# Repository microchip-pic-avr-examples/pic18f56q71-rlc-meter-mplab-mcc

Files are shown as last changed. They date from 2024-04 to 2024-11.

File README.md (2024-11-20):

<!-- Please do not change this html logo with link -->

<a href="https://www.microchip.com" rel="nofollow">MCHP</a>

# RLC Meter Using the PIC18F56Q71 Microcontroller with MCC Melody

This repository contains an MPLAB® X project, a Resistance, Inductance, Capacitance (RLC) meter implementation using the internal resources of PIC18F56Q71 microcontroller.  
In this code example, the PIC18F56Q71 microcontroller will be used to implement a RLC meter using the Analog-to-Digital Converter (ADC) with Computation and Context, Direct Memory Access (DMA), Timers (TMR0, TMR2, TMR4) and Configurable Logic Cell (CLC) peripherals. The sinusoidal waveform is generated using the Pulse-Width Modulator with Compare (PWM) and other peripherals on the device (DMA, timers). The measurement will be displayed using serial protocols.

**Note**: This project is not an measurement instrument, it was developed only for educational purpose.

## Related Documentation
- [PIC18F56Q71 Product Page](https://www.microchip.com/en-us/product/PIC18F56Q71?utm_source=GitHub&utm_medium=TextLink&utm_campaign=MCU8_PIC18-Q71&utm_content=pic18f56q71-rlc-meter-mplab-mcc-github&utm_bu=MCU08)
- [PIC18F56Q71 Code Examples on Discover](https://mplab-discover.microchip.com/v2?dsl=PIC18F56Q71)
- [PIC18F56Q71 Code Examples on GitHub](https://github.com/microchip-pic-avr-examples/?q=PIC18F56Q71)

## Software Used

- [MPLAB X IDE v6.20 or newer](https://www.microchip.com/en-us/tools-resources/develop/mplab-x-ide?utm_source=GitHub&utm_medium=TextLink&utm_campaign=MCU8_PIC18-Q71&utm_content=pic18f56q71-rlc-meter-mplab-mcc-github&utm_bu=MCU08)
- [MPLAB® XC8 v2.50 or newer](https://www.microchip.com/en-us/tools-resources/develop/mplab-xc-compilers?utm_source=GitHub&utm_medium=TextLink&utm_campaign=MCU8_PIC18-Q71&utm_content=pic18f56q71-rlc-meter-mplab-mcc-github&utm_bu=MCU08)
- [PIC18F-Q_DFP 1.25.433](https://packs.download.microchip.com/)

## Hardware Used

- The [PIC18F56Q71 Curiosity Nano Development board](https://www.microchip.com/en-us/development-tool/EV01G21A?utm_source=GitHub&utm_medium=TextLink&utm_campaign=MCU8_PIC18-Q71&utm_content=pic18f56q71-rlc-meter-mplab-mcc-github&utm_bu=MCU08) is used as a test platform:
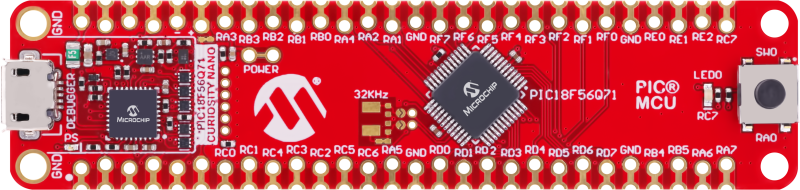
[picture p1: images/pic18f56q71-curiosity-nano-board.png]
    <br>

- [Curiosity Nano Adaptor](https://www.microchip.com/en-us/development-tool/AC164162?utm_source=GitHub&utm_medium=TextLink&utm_campaign=MCU8_PIC18-Q71&utm_content=pic18f56q71-rlc-meter-mplab-mcc-github&utm_bu=MCU08)
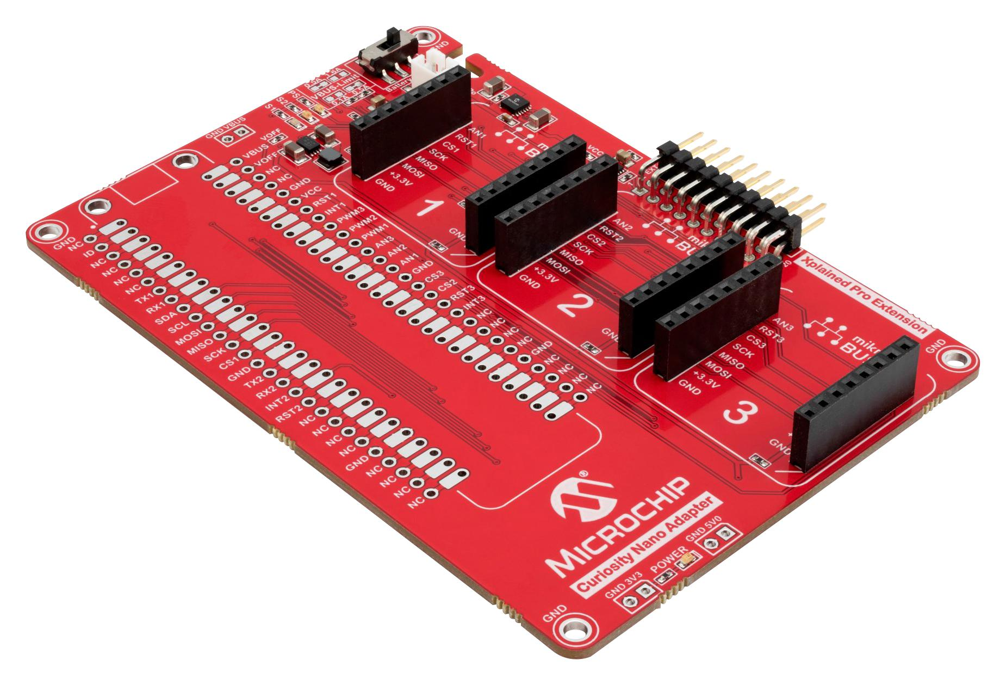
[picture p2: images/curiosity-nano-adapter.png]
    <br>

- [OLED C CLICK Board](https://www.mikroe.com/oled-c-click#/263-clickid-yes) (mikroBUS socket 3)
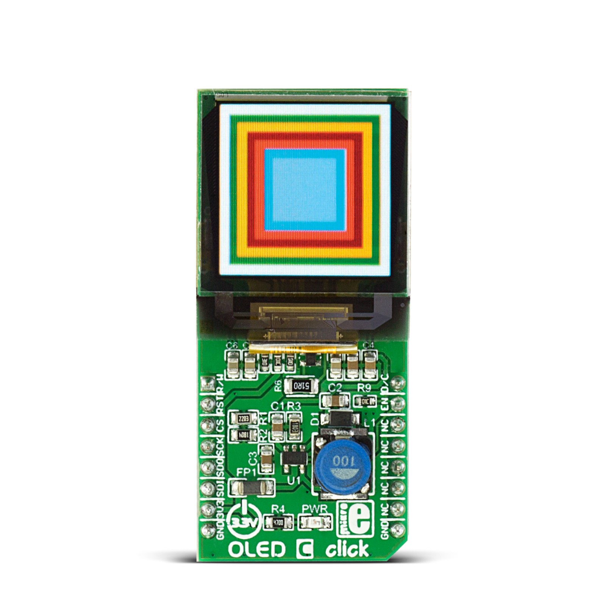
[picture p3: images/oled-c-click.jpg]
    <br>

- RLC Meter Click Board (mikroBUS socket 1)
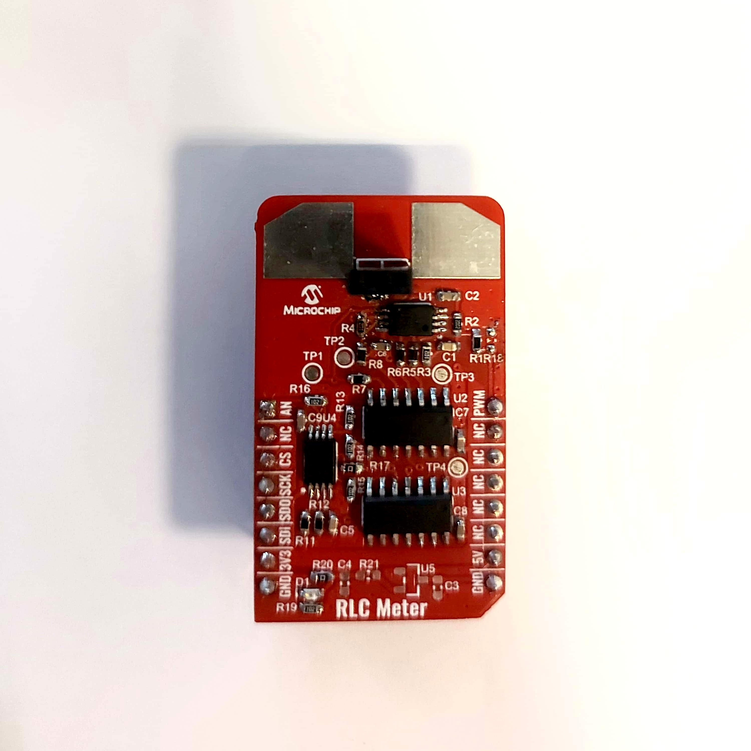
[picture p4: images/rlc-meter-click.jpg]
    <br>

## Operation

To program the Curiosity Nano board with this MPLAB X project, follow the steps provided in the [How to Program the Curiosity Nano Board](#how-to-program-the-curiosity-nano-board) section.

## Concept

RLC meters are measuring instruments that measure a physical property known as impedance. Impedance, which is expressed using the quantifier Z, indicates resistance to the flow of an alternating current (AC). It can be calculated from the current (I) flowing to the measurement target and the voltage (V) across the target’s terminals. Since impedance is expressed as a vector on a complex plane, RLC meters measure not only the ratio of current and voltage RMS values, but also the phase difference between current and voltage waveforms. The result of the measurement is displayed using an OLED display or the UART2 peripheral.

### Measurement Principle

There are different methods used to measure the impedance, each of them with advantages and disadvantages:
- Auto-Balancing Bridge Method
- Resonant Method
- I-V Method

This demo uses an auto-balancing bridge which is the measurement circuit in many RLC meters. The circuit has four terminals, all of which are connected to the measurement target. The following image shows the concept used for this method. The OPAMP implements the automatic balanced bridge that was mentioned above. The principle behind this method is to determine the impedance by measuring the current and voltage.
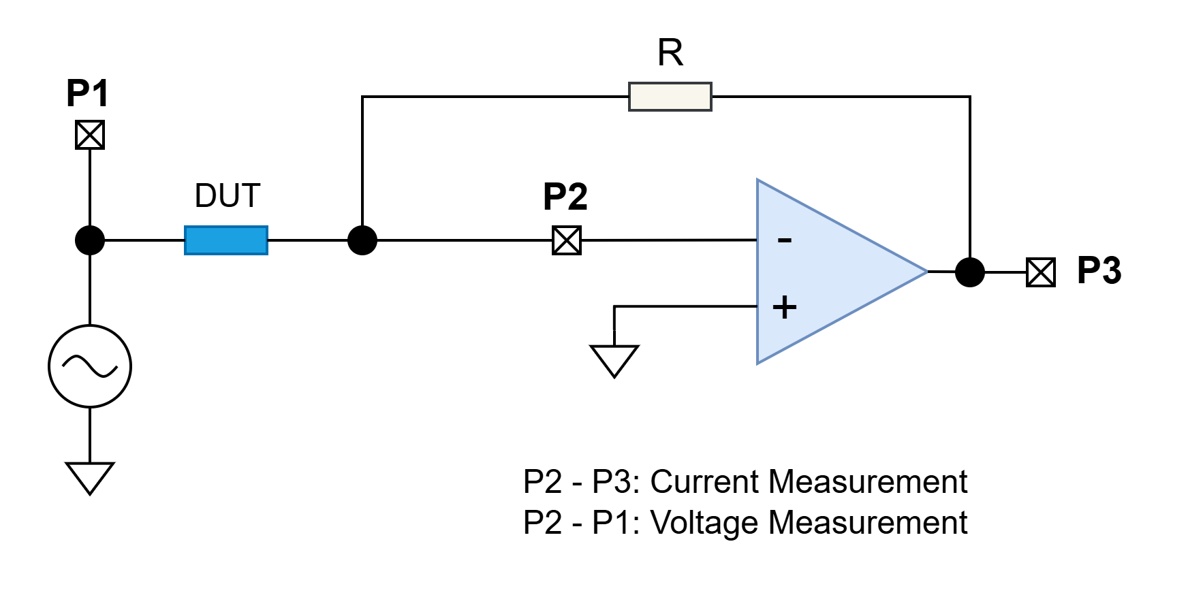
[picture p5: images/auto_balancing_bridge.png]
<br>

### Sinusoidal Waveform Generation

The sinusoidal waveform is generated using the PWM2 peripheral. The PWM duty-cycle is updated using a sine Look-Up Table (LUT) that is stored into the Flash Program memory (const uint8_t waveROM250[250]). The resulted waveform is then filtered using an external low-pass filter to obtain the sinusoidal signal. To ensure precise timing for each sample, a DMA channel (DMA2) triggered by CLC1 is used to transfer data from the sine table to PWM2. The PWM2 frequency is set to 1 MHz, meaning that for the maximum frequency of the resulted sine wave of 1 KHz, the PWM duty-cycle is updated in 250 steps at every four PWM periods, ensuring a stable output. The generated sinusoidal signal frequency can easily be modified by changing the number of PWM periods after the duty-cycle is updated. This is done by changing the TMR0 period with the formula below. The multiplication with the `2` factor is done because the TMR0 output is used in a Divide-by-Two circuit implemented with the CLC8 peripheral.

<br>

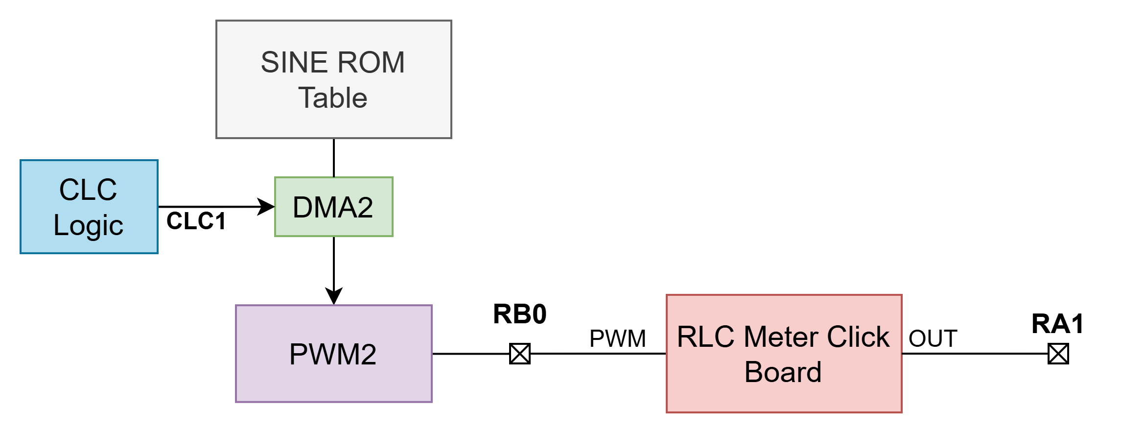
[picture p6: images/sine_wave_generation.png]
<br>

The sine wave frequency can be modified in the program using the `FREQ` macro. The possible values are between 100 Hz and 1 KHz. For better results, it is recommended to use lower frequency (e.g. 100 Hz) for capacitance measurement and higher frequency for inductance.

### Measurement board

The measurement circuit is realised on a board that can be used on a mikroBUS™ socket. The entire schematic and Gerber files of the board can be found in the `Board Documents` folder.

The following image shows the schematic of the low-pass filter and auto-balancing bridge. A [MCP6022](https://www.microchip.com/en-us/product/mcp6022?utm_source=GitHub&utm_medium=TextLink&utm_campaign=MCU8_PIC18-Q71&utm_content=pic18f56q71-rlc-meter-mplab-mcc-github&utm_bu=MCU08) is used for the two OPAMPs. The first one is used for the filter that generates the sine wave from the PWM signal. The second one implements the automatic balanced bridge that was mentioned above. The device under test (DUT) is connected in the circuit using the J1 connector.
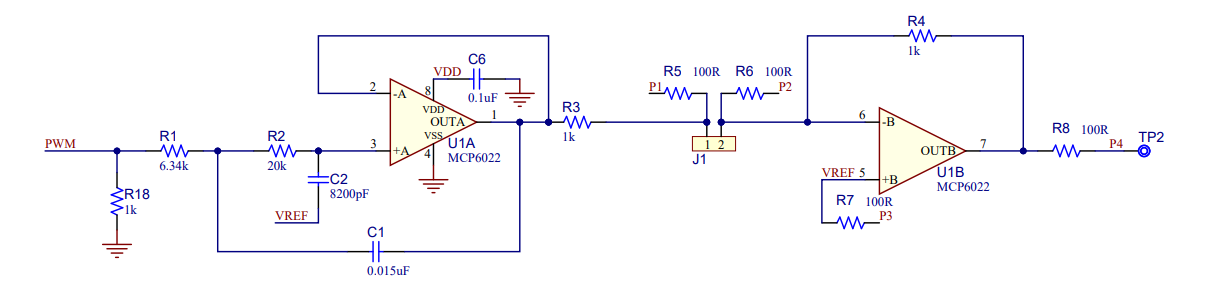
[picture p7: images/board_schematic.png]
<br>
<br>**Note:** The R18 resistor is not connected on the board.

The selection between the current and voltage acquisition is done using two [MCP6S26](https://www.microchip.com/en-us/product/mcp6s26?utm_source=GitHub&utm_medium=TextLink&utm_campaign=MCU8_PIC18-Q71&utm_content=pic18f56q71-rlc-meter-mplab-mcc-github&utm_bu=MCU08) PGAs that have an internal multiplexer used to select between the six possible inputs. The PGAs multiplexers for input and gain selection can be programmed using the Serial Peripheral Interface (SPI) and they are connected in a daisy-chain configuration. The two PGAs have multiple inputs connected for different configurations of the circuit. The following configuration is used for this application:

|**Measurement**|**PGA1 (U2) Channel**|**PGA2 (U3) Channel**| 
| :-------:     | :-----------------: | :-----------------: |
|    Current    |         CH3         |         CH2         | 
|    Voltage    |         CH1         |         CH2         |  

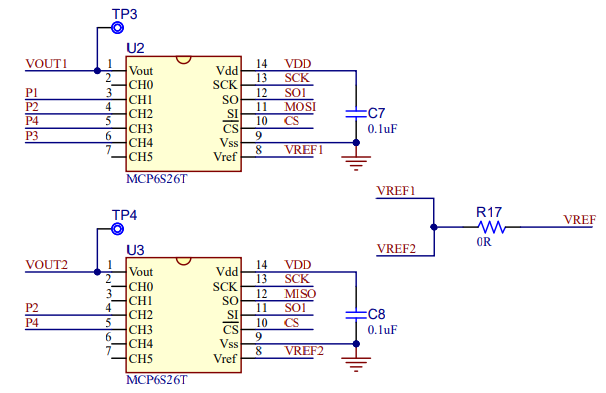
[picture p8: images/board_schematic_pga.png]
<br>
<br>**Note:** The R17 resistor offers the possibility to connect the VREF of the two PGAs together (R17 not connected) or to the board VREF (R17 connected). In this case, the R17 resistor is connected.

A second [MCP6022](https://www.microchip.com/en-us/product/mcp6022?utm_source=GitHub&utm_medium=TextLink&utm_campaign=MCU8_PIC18-Q71&utm_content=pic18f56q71-rlc-meter-mplab-mcc-github&utm_bu=MCU08) is used for the VREF signal and to obtain the output signal. The VREF is set to VDD/2, meaning 1.65 V. The second OPAMP is used in differential to single-ended configuration to obtain a single output from the two PGAs that is used for the ADC input.
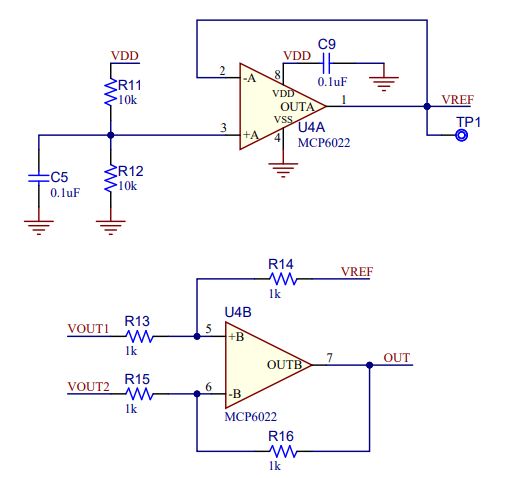
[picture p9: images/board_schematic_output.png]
<br>

The board is used at 3.3 V. The power source can be selected using the R20 and R21 resistors. By connecting the R20 resistor, the board is powered from the 3V3 pin on the mikroBus socket. By connecting the R21 resistor, the board is powered from an external LDO (such as [MCP1700](https://www.microchip.com/en-us/product/mcp1700?utm_source=GitHub&utm_medium=TextLink&utm_campaign=MCU8_PIC18-Q71&utm_content=pic18f56q71-rlc-meter-mplab-mcc-github&utm_bu=MCU08)) that is connected to the 5V pin on the mikroBus socket and offers 3V3 output.
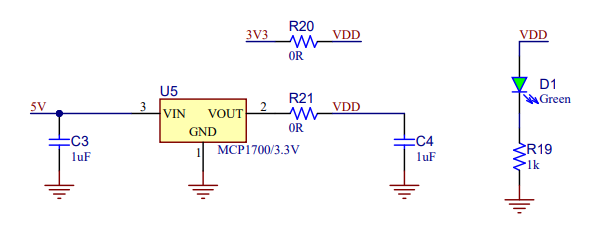
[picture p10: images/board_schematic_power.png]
<br>
<br>**Note:** Just one resistor (R20 or R21) must be connected on the board. R20 resistor is connected on the presented one.

### Synchronization Between the Generated Signal and the Data Acquired

To allow accurate values for computed impedance, the acquisition of the samples for current and voltage must be synchronized with input signal (generated waveform). The synchronization between generated waveform and acquired samples is done using on-chip peripherals like CLCs, Pulse-Width Modulation (PWM) and timers:
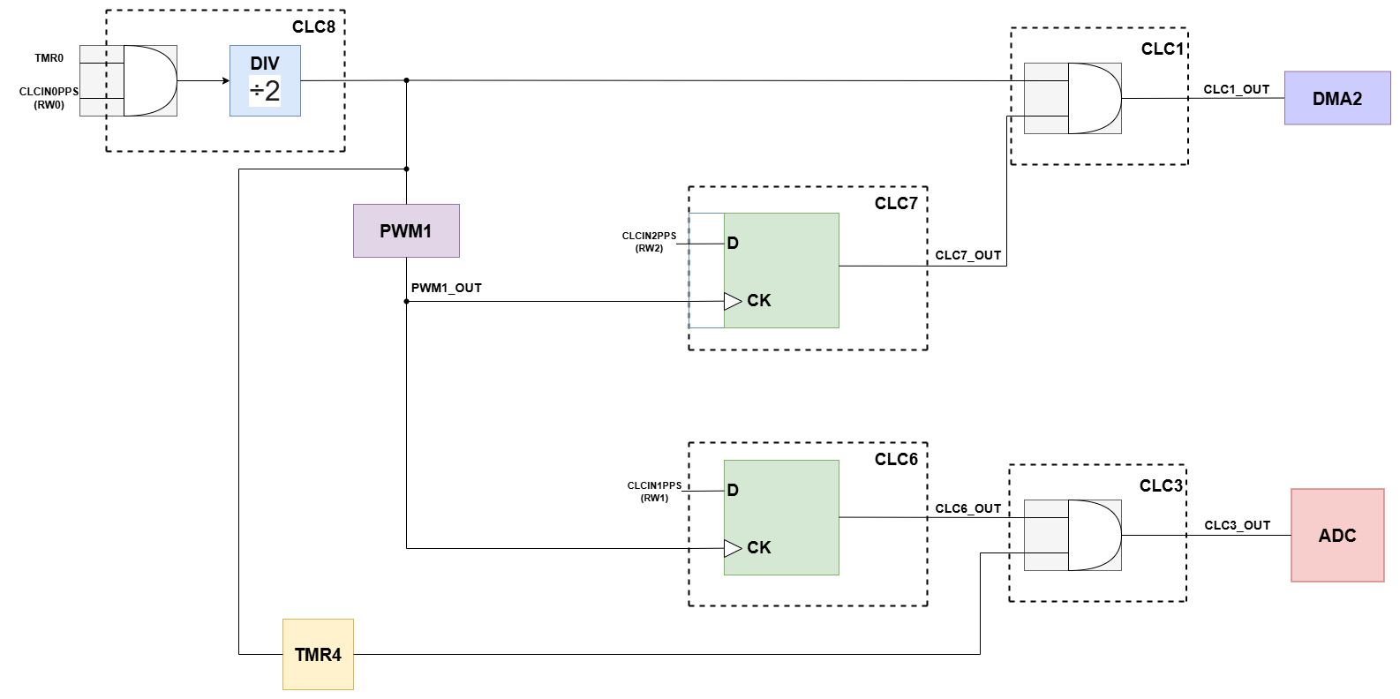
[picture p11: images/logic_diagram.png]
<br>

The TMR4 peripheral is used for oversampling to increase the acquiring rate of the waveform. The sampling rate can be configured using the `TIMESAMPLING_RATE` macro.

### Waveform Acquisition

The MCP6S26 input multiplexer is used to select between the current and voltage acquisition. For an impedance measurement, two of those acquisitions are performed starting with the voltage one. For both of them, the samples are saved in different buffers using alternatively DMA1/DMA3 peripherals. To calculate the real and imaginary parts for voltage and current, the processed data is multiplied by cosinus wave and sinus wave, respectively. The results are then scaled using the gain values. The DAC1 peripheral is used to eliminate the DC component of the signal.

The usage of oversampling means that more periods of the sinusoidal signal are used for the acquisition (the number is equal to the time sampling rate) and the samples are not acquired in order for a reconstruction of a single sine wave. To calculate the real and imaginary parts described above, the acquired samples are read in the order of acquisition and the corresponding cosinus/sinus value for each sample is determined based on the chosen sampling rate. 
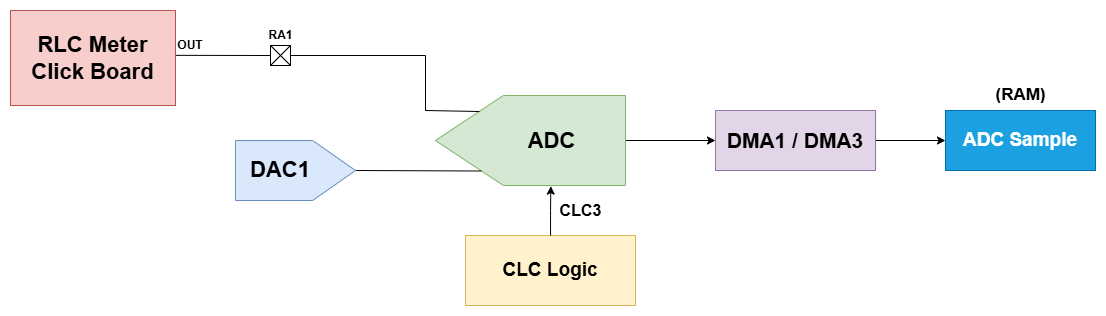
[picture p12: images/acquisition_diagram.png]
<br>

### Calibration and Auto Gain

The MCP6S26 gain selection multiplexer is used to implement an auto gain algorithm when a new component is inserted to independently determine the right gain for voltage and current measurements. The principle is to adjust the gain to obtain the maximum amplification that does not saturate the output. The maximum value for voltage is determined when the DUT is not connected and for the current by measuring in short circuit. The measured values are then increased with 40%. The values used for comparisons in the algorithm are the raw read data, that are not scaled using the gain factor.

The maximum values are automaticaly determined using a calibration process and the determined values are then stored into the on-board EEPROM by using the Nonvolatile Memory Module (NVM) peripheral. This way, when the application is started, it verifies if there are calibration data stored in EEPROM by reading and verifying a byte that is stored at a known address. If the calibration data are available, they are read, stored in variables and used in the auto gain algorithm described above. If they are not available, the user can start the calibration for voltage and current by short pressing the on-board button and following the displayed instructions. The user can also begin the calibration process when the application is already running with a long press of the button. TMR2 peripheral is used for detection of the short and long press of the button.
 
## Setup

The following peripheral and clock configurations are set up using the MPLAB Code Configurator (MCC) Melody for the PIC18F56Q71:

1. Clock Control:
    - Clock Source: HFINTOSC
    - HF Internal Clock: 64_MHz
    - Clock Divider: 1
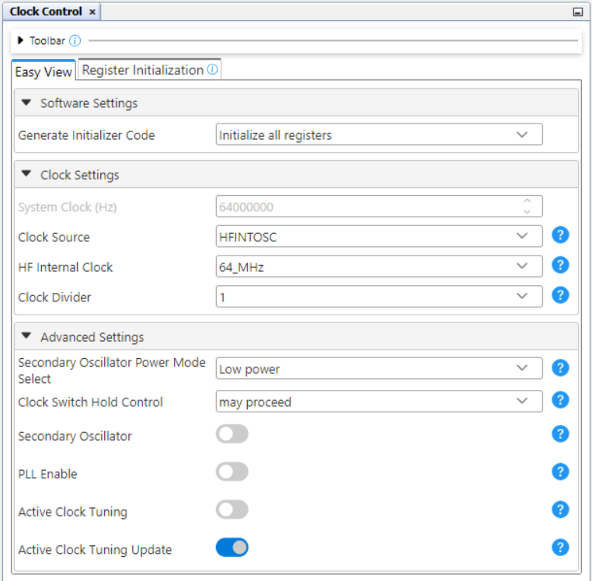
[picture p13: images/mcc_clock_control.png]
    <br>

2. DMA1:
    - DMA Enable: Enabled
    - Start Trigger: ADCH1
    - Source Region: SFR
    - Source module: ADC
    - Source SFR: ADRESL_CX1
    - Source Mode: incremented
    - Source Message Size: 2
    - Source Counter Reload Action: SIRQEN is not cleared
    - Destination Region: GPR
    - Destination Variable: adcSamplesArray1
    - Destination Size: 512
    - Destination Mode: incremented
    - Destination Message Size: 500
    - Destination Counter Reload Action: SIRQEN is cleared
    - Interrupt Driven: Enabled
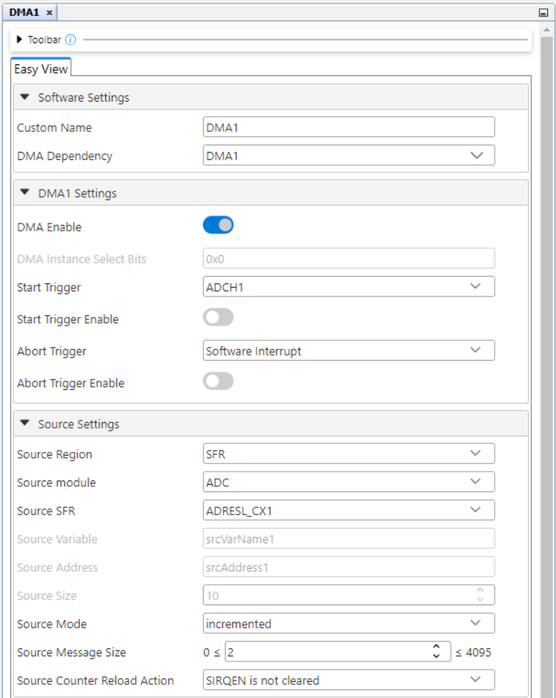
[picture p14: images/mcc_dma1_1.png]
    <br>
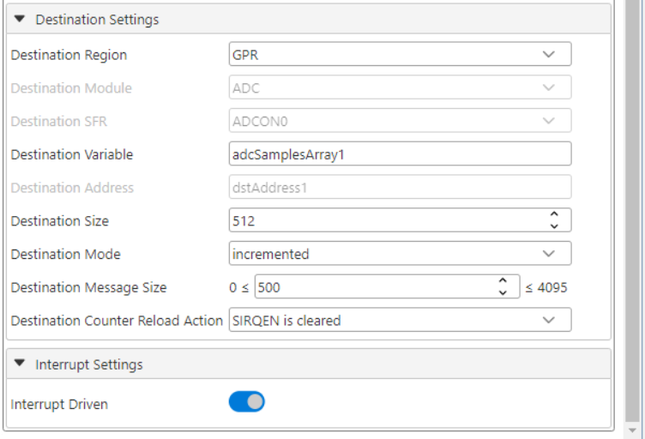
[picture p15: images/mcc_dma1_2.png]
    <br>
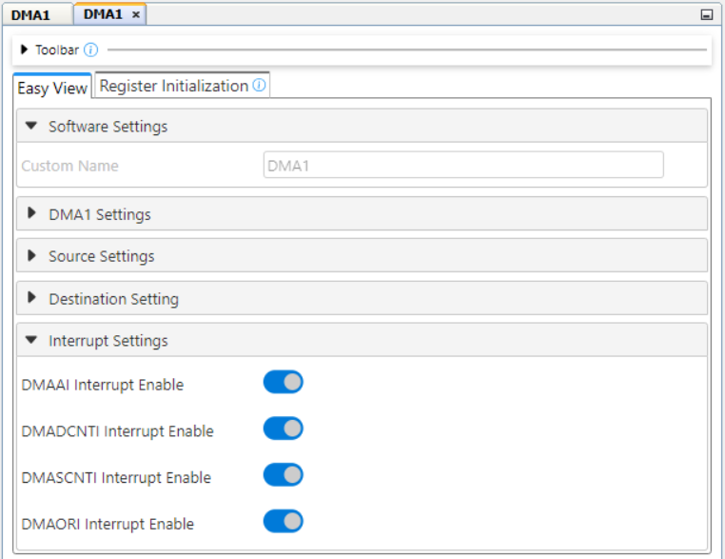
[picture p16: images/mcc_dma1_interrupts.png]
    <br>

3. DMA2:
    - DMA Enable: Enabled
    - Start Trigger: CLC1
    - Start Trigger Enable: Enabled
    - Source Region: Program Flash
    - Source Address: 0x001000
    - Source Mode: incremented
    - Source Message Size: 250
    - Source Counter Reload Action: SIRQEN is not cleared
    - Destination Region: SFR
    - Destination Module: PWM2_16BIT
    - Destination SFR: PWM2S1P1L
    - Destination Mode: unchanged
    - Destination Message Size: 1
    - Destination Counter Reload Action: SIRQEN is not cleared
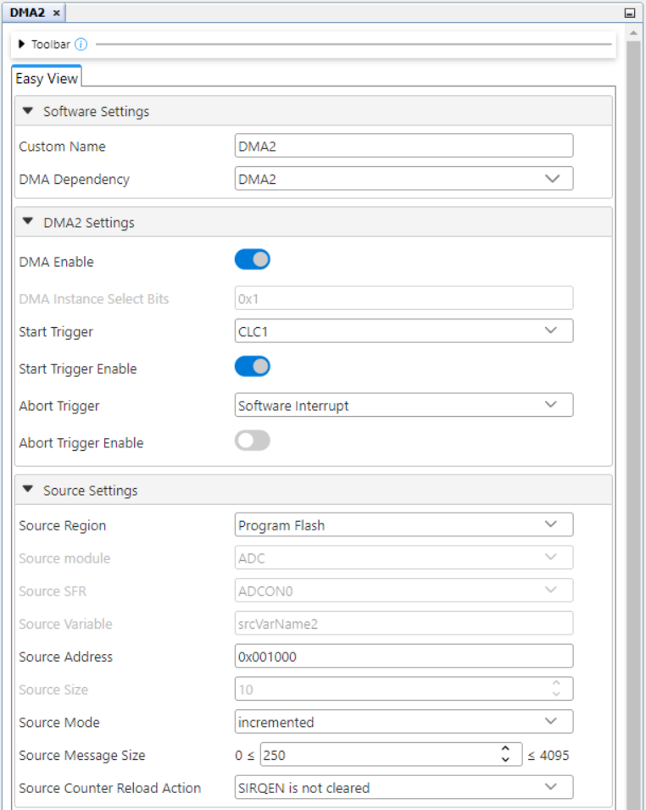
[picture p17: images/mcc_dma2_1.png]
    <br>
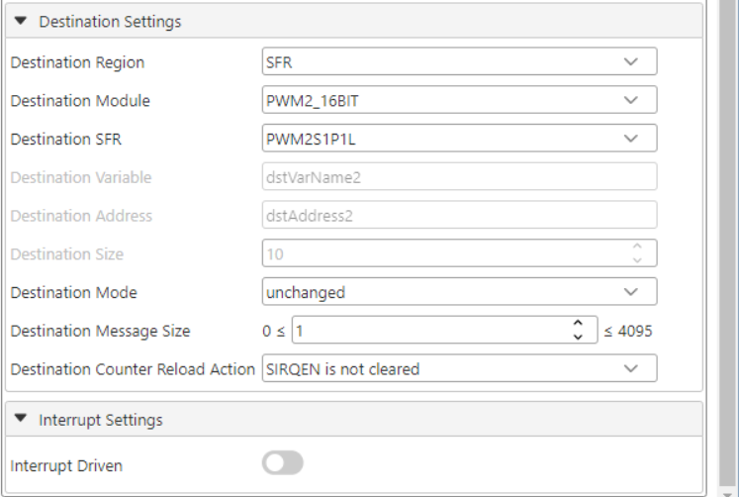
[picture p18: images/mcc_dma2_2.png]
    <br>

4. DMA3:
    - DMA Enable: Enabled
    - Start Trigger: ADCH1
    - Source Region: SFR
    - Source module: ADC
    - Source SFR: ADRESL_CX1
    - Source Mode: incremented
    - Source Message Size: 2
    - Source Counter Reload Action: SIRQEN is not cleared
    - Destination Region: GPR
    - Destination Variable: adcSamplesArray3
    - Destination Size: 512
    - Destination Mode: incremented
    - Destination Message Size: 500
    - Destination Counter Reload Action: SIRQEN is cleared
    - Interrupt Driven: Enabled
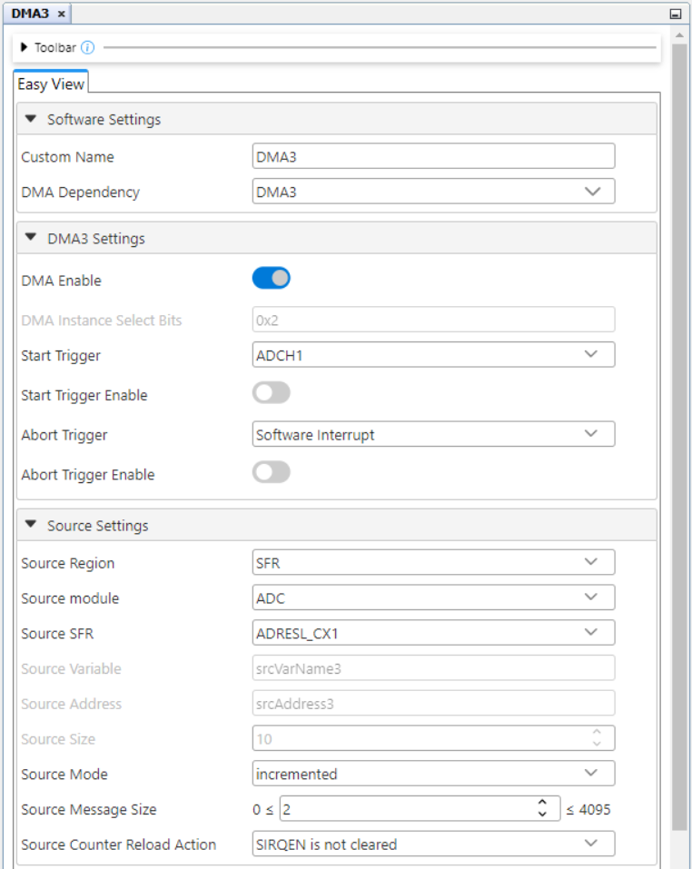
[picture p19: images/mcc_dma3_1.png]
    <br>
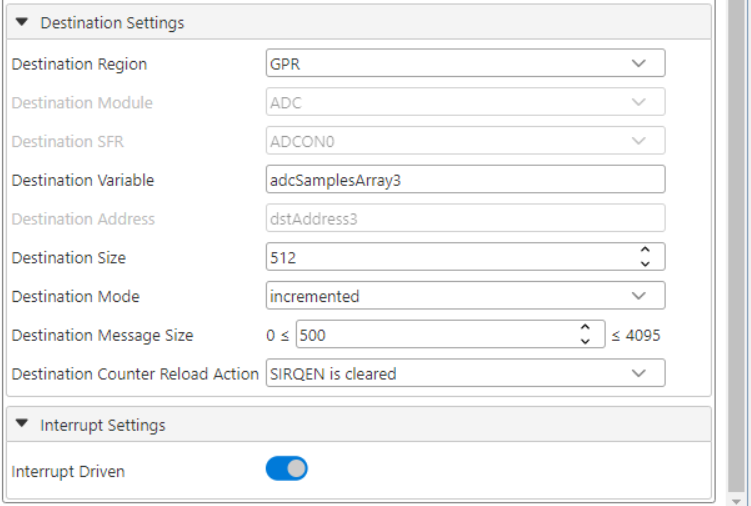
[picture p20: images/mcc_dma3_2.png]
    <br>
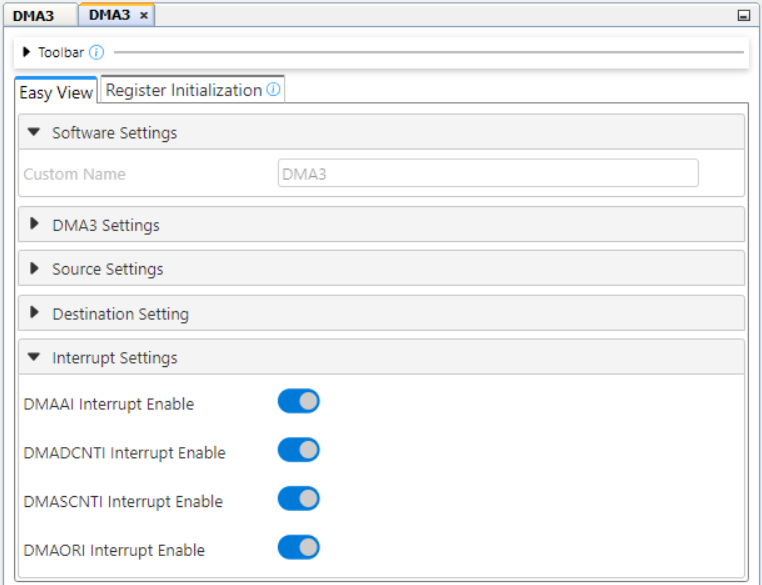
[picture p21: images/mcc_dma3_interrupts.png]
    <br>

5. DAC1:
    - Vdd: 3.3
    - Required Voltage Ref: 1.65
    - DAC Enable: Enabled
    - DAC Positive reference selection: VDD
    - DAC Negative reference selection: VSS
    - DAC Output Enable Selection: DACOUT1 and DACOUT2 are Disabled
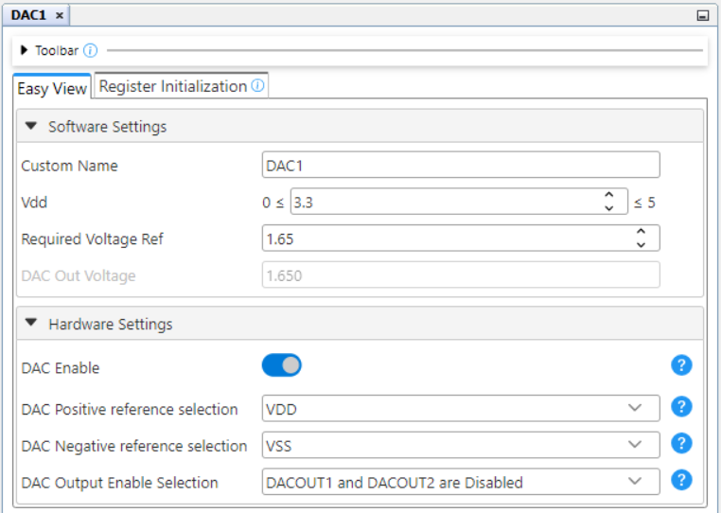
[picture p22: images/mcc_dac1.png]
    <br>

6. ADC:
    - ADC: Enabled
    - Input Configuration: Differential
    - Result Format: right justified, two's compliment
    - Auto-conversion Trigger Source: CLC3
    - Clock Selection: FOSC
    - Clock Divider: FOSC/64
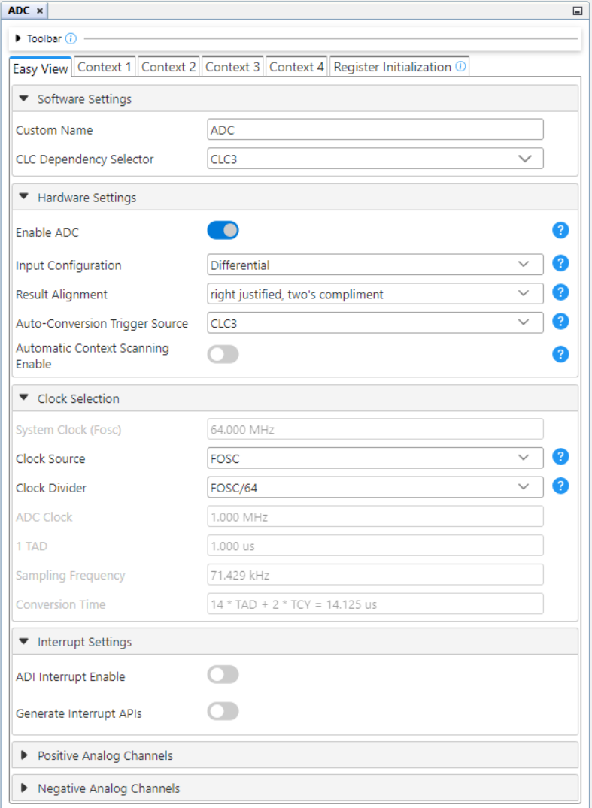
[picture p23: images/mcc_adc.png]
    <br>

7. ADC Context 1
    - Positive Channel Selection: ANA1
    - Positive Voltage Reference: VDD
    - Negative Channel Selection: DAC1
    - Negative Voltage Reference: VSS
    - Computation mode: Basic_mode
    - Threshold Interrupt Mode: Enabled
    - Upper Threshold: 1
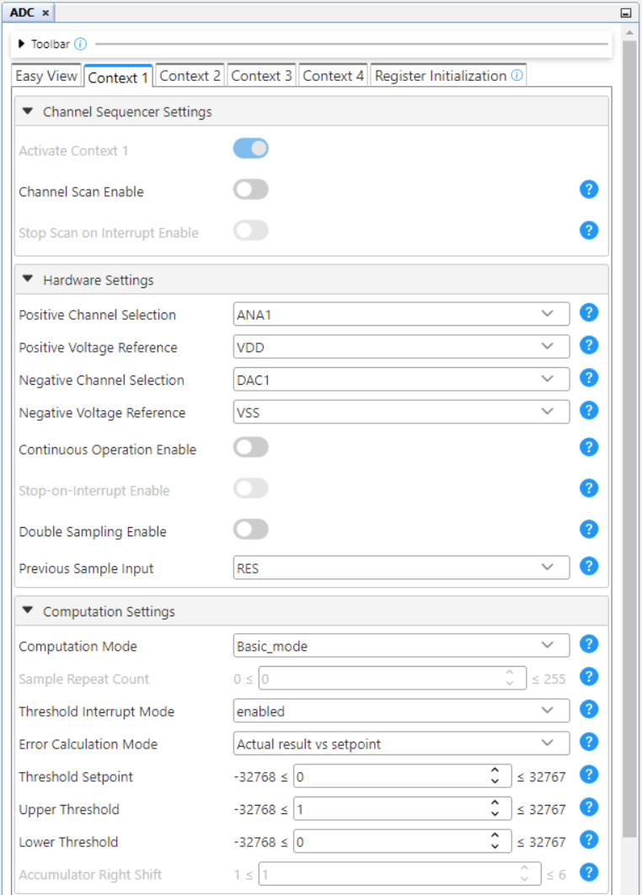
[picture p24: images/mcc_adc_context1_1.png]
    <br>

8. TMR0
    - Enable Timer: Enabled
    - Timer Mode: 8-bit
    - Clock Source: HFINTOSC
    - Clock Prescaler: 1:8
    - Postscaler: 1:1
    - Requested Period: 2 μs
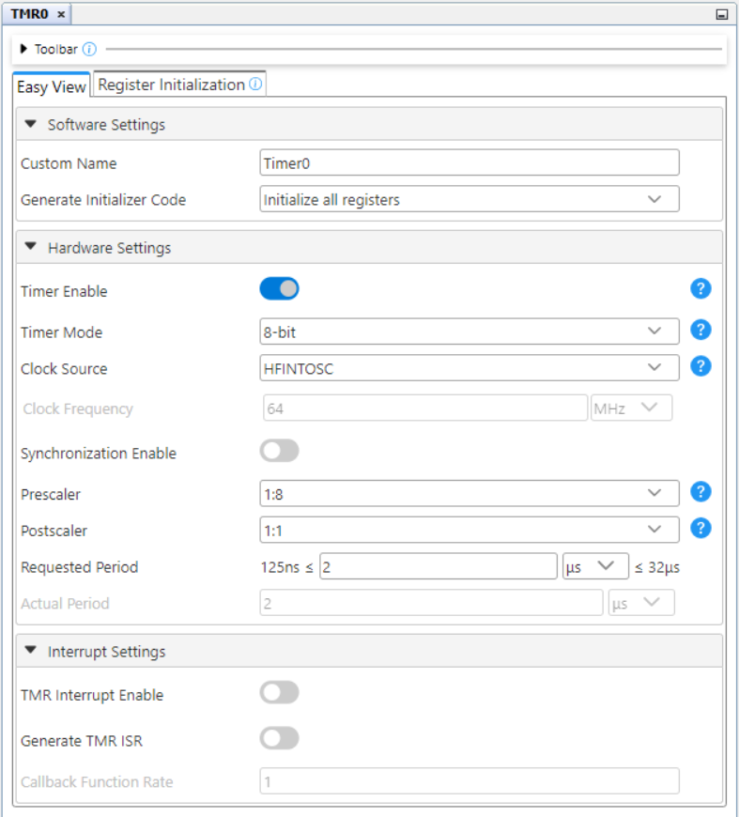
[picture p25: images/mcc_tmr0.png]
    <br>

9. TMR2
    - Enable Timer: Disabled
    - Control Mode: Roll over pulse
    - Clock Source: LFINTOSC
    - Prescaler: 1:32
    - Postscaler: 1:4
    - Requested Period: 1 s
    - TMR Interrupt Enable: Enabled
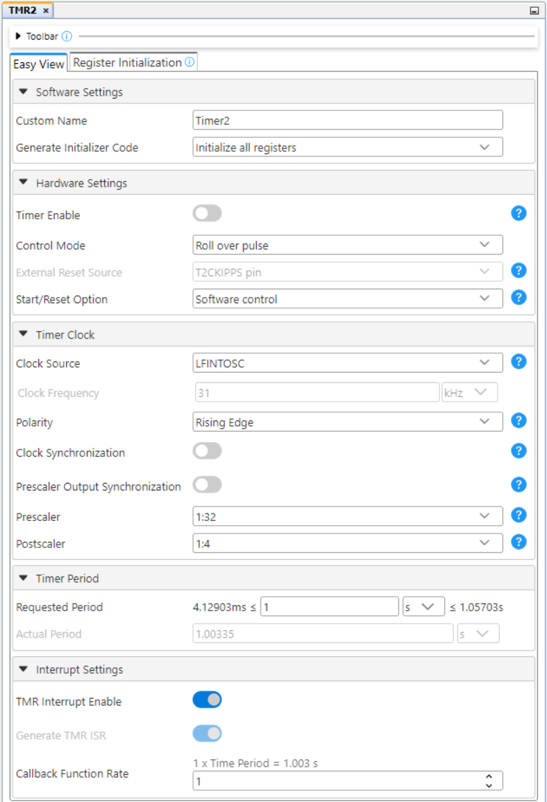
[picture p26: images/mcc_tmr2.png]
    <br>

10. TMR4
    - Enable Timer: Enabled
    - Control mode: Roll over pulse
    - External Reset Source: CLC6_out
    - Start/Reset Option: Resets at TMR4_ers=0
    - Clock Source: CLC8_OUT
    - Clock Frequency: 250 kHz
    - Prescaler: 1:1
    - Postscaler: 1:1
    - Requested Period: 44 μs
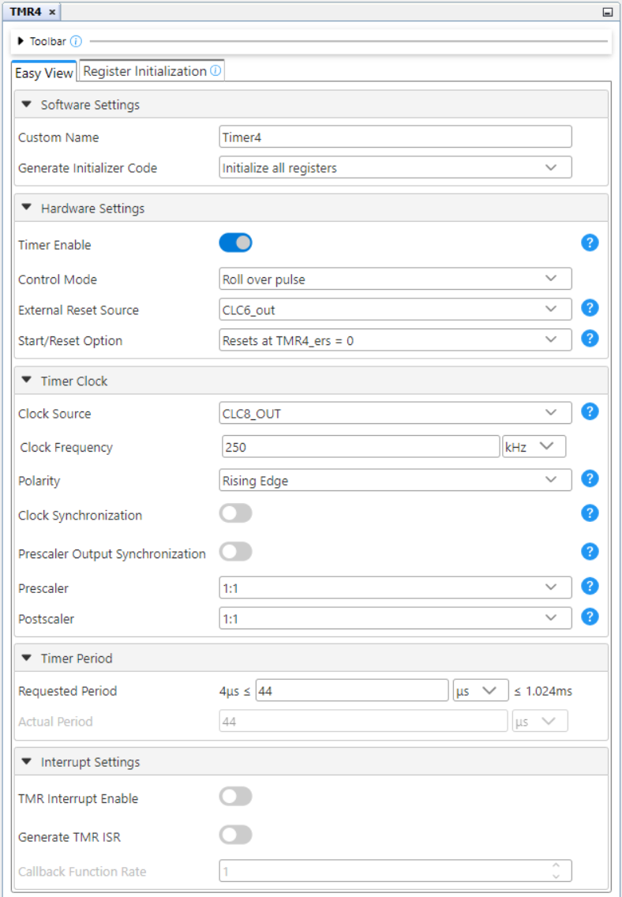
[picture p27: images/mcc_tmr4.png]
    <br>

11. PWM1_16BIT
    - Enable PWM: Enabled
    - Clock Source: CLC8_OUT
    - Clock Frequency(KHz): 250
    - Mode: Left aligned mode
    - Requested Frequency(KHz): 1
    - Output1 Duty Cycle(%): 50
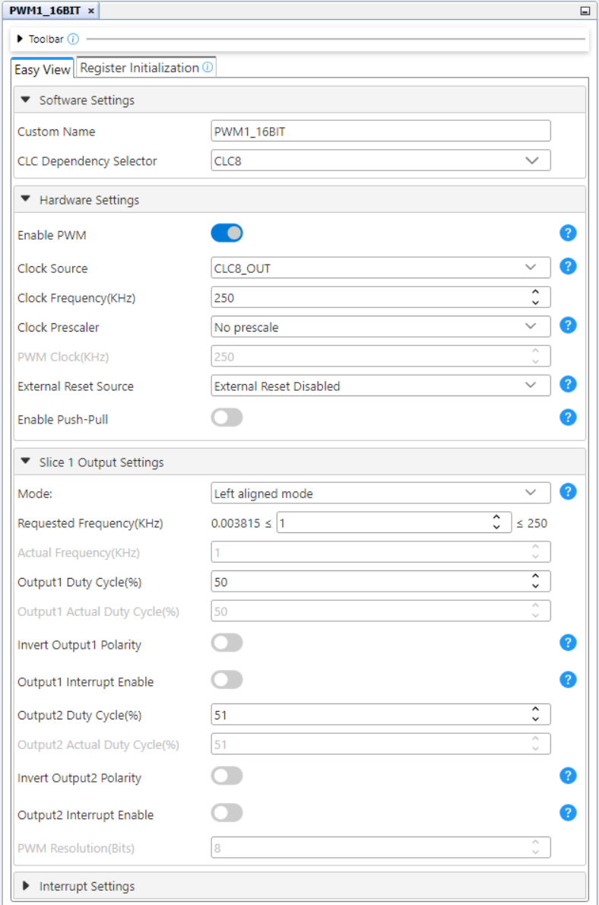
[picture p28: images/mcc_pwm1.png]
    <br>

12. PWM2_16BIT
    - Enable PWM: Enabled
    - Clock Source: FOSC
    - Mode: Left aligned mode
    - Requested Frequency(KHz): 1000
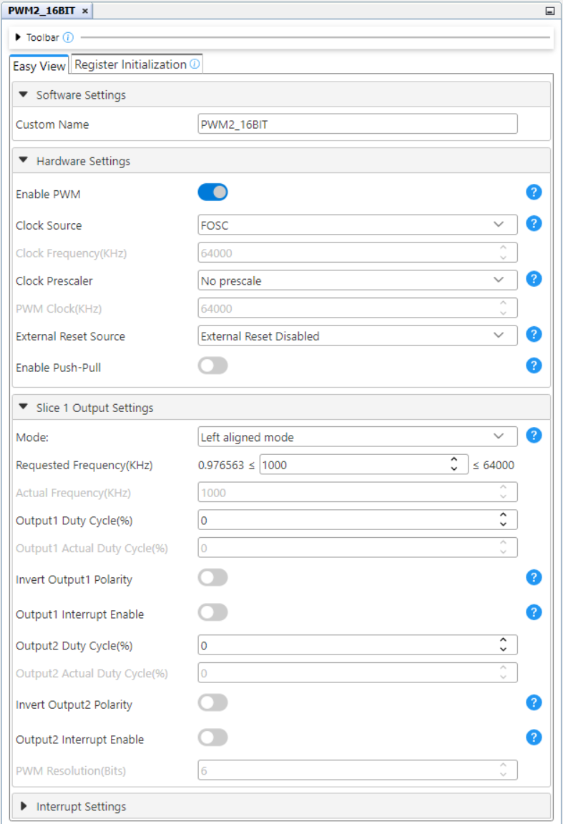
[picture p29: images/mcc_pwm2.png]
    <br>

13. CLC1
    - Enable CLC: Enabled
    - Logic Cell Mode bits: AND-OR
    - Enable Rising Interrupt: Enabled
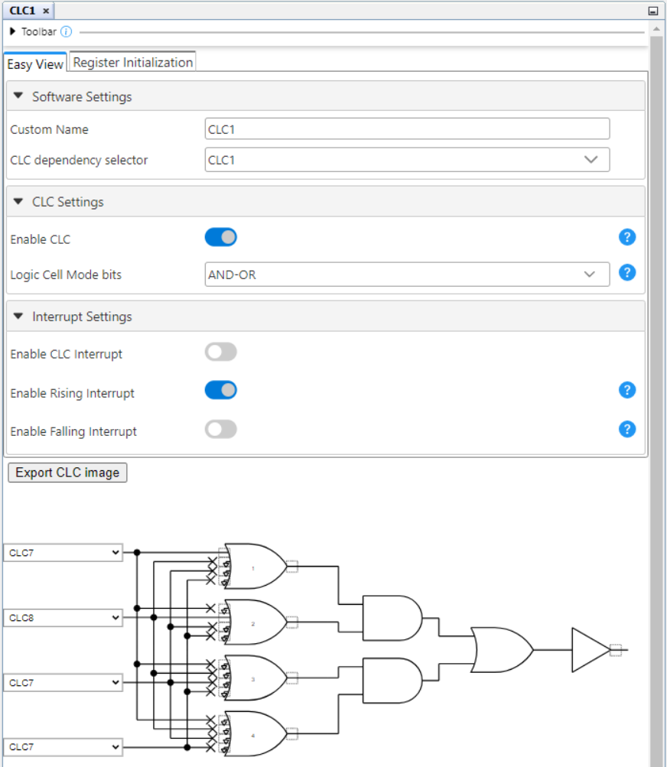
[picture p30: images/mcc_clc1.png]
    <br>

14. CLC3
    - Enable CLC: Enabled
    - Logic Cell Mode bits: AND-OR
    - Enable Rising Interrupt: Enabled
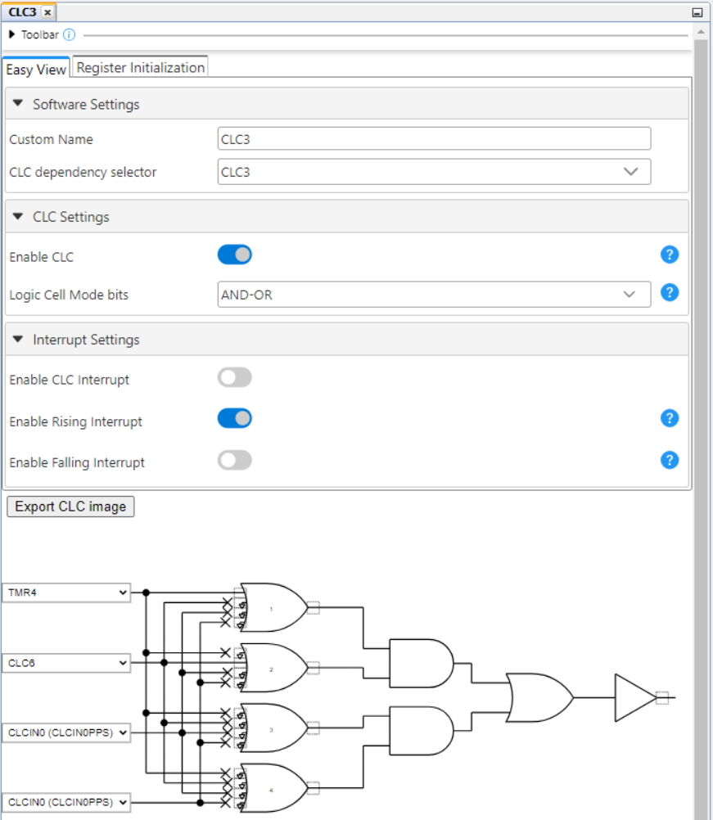
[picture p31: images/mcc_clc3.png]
    <br>

15. CLC6
    - Enable CLC: Enabled
    - Logic Cell Mode bits: 1-input D flip-flop with S and R
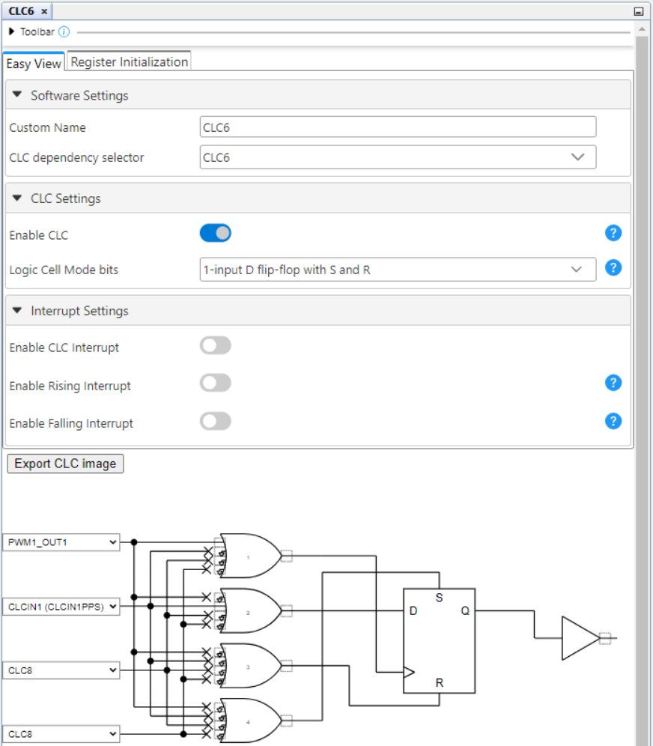
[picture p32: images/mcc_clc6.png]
    <br>

16. CLC7
    - Enable CLC: Enabled
    - Logic Cell Mode bits: 1-input D flip-flop with S and R
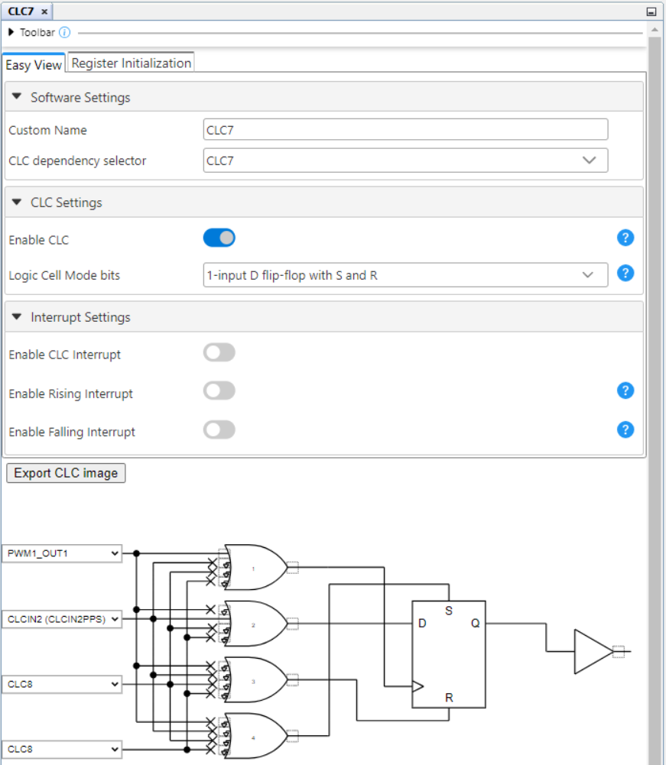
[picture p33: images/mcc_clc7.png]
    <br>

17. CLC8
    - Enable CLC: Enabled
    - Logic Cell Mode bits: 1-input D flip-flop with S and R
    - Enable Rising Interrupt: Enabled
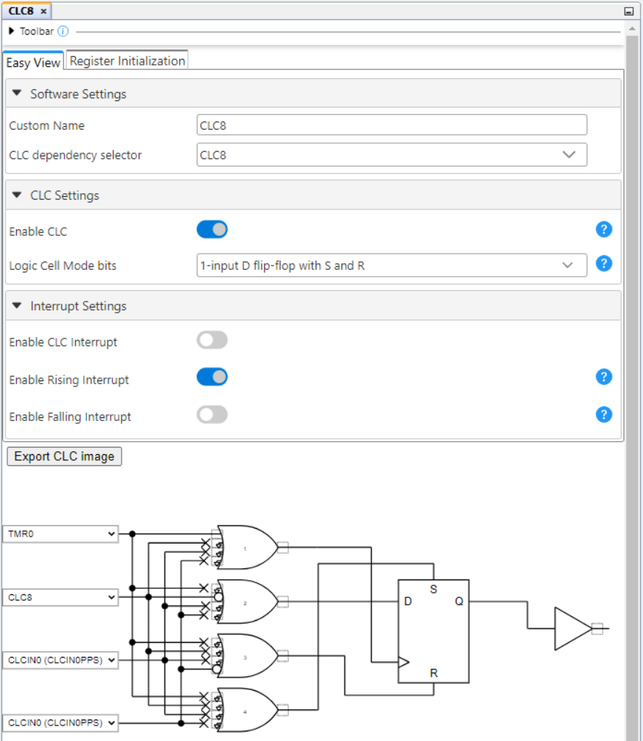
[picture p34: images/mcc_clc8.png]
    <br>

18. SPI1
    - Clock Source: FOSC
    - Clock Frequency (Hz): 64000000
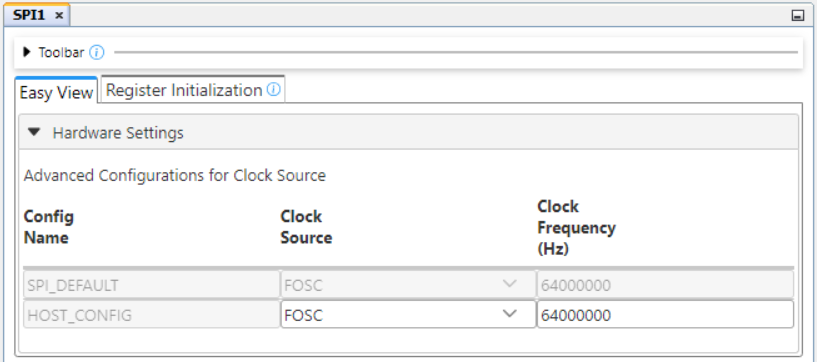
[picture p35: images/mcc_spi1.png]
    <br>

19. SPI1_Host
    - Config Name: HOST_CONFIG
    - Requested Speed (KHz): 1000
    - Mode: Mode 0
    - Data Input Sample At: Middle
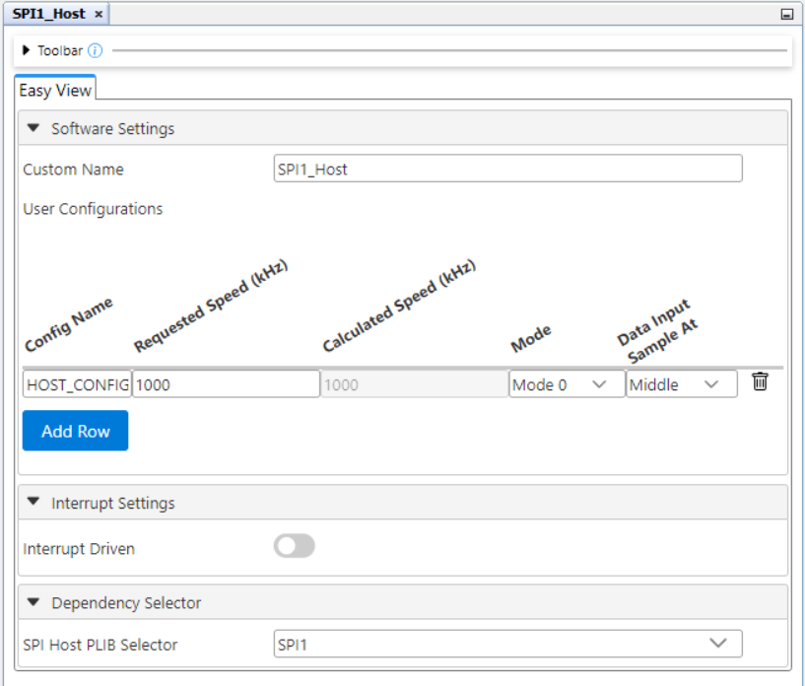
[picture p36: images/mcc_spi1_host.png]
    <br>

20. UART2
    - Requested Baudrate: 115200
    - Parity: None
    - Data Size: 8
    - Stop Bits: 1
    - Redirect Printf to UART: Enabled
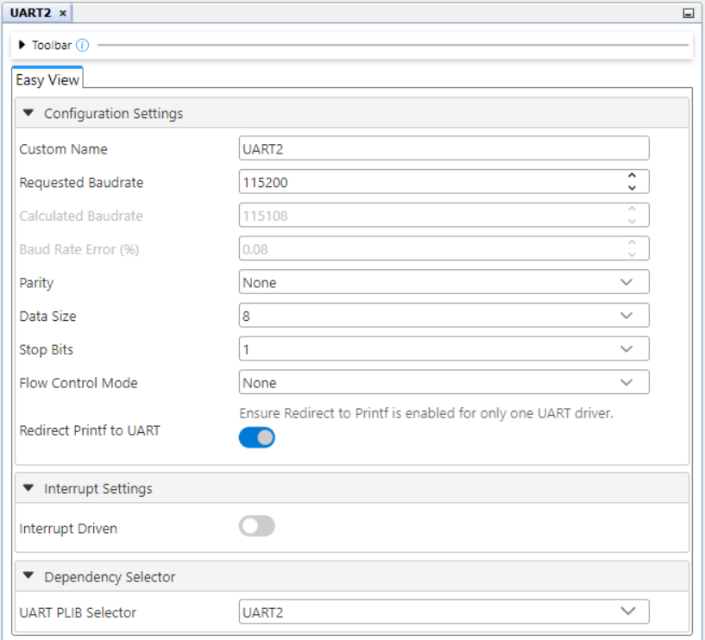
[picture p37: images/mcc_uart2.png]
    <br>

21. UART2PLIB
    - Enable Receive: Enabled
    - Enable Transmit: Enabled
    - Enable UART: Enabled
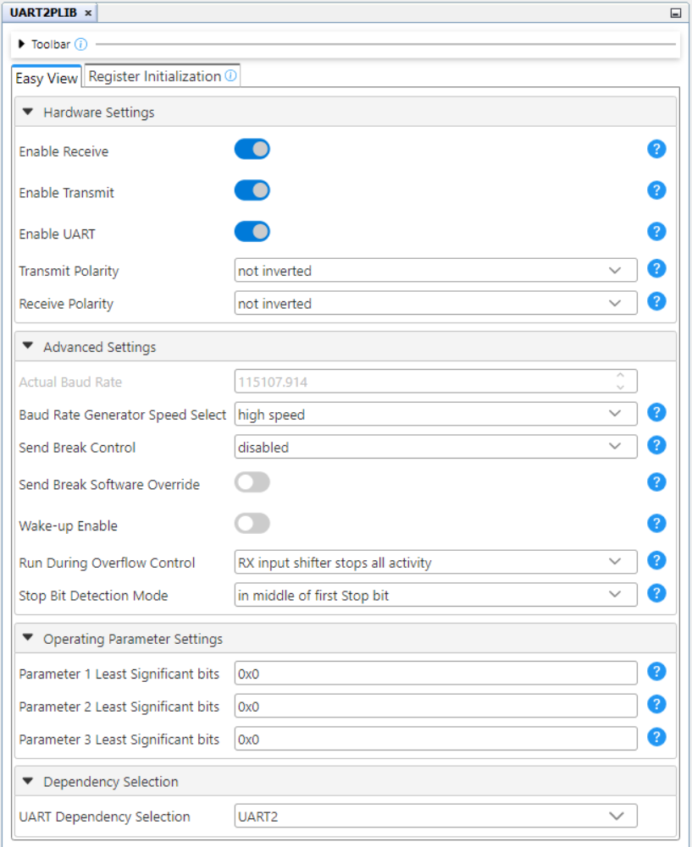
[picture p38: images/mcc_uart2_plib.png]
    <br>

22. NVM
    - Generate EEPROM APIs: Enabled
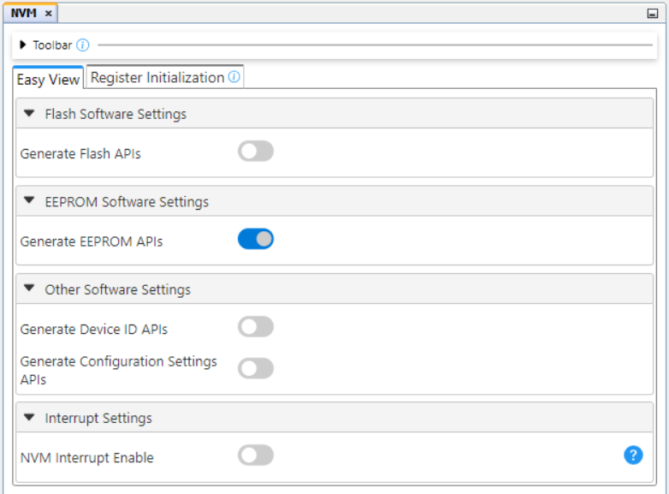
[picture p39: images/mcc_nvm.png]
    <br>

23. CPU
    - DMA1 Priority Register: priority level 4
    - DMA2 Priority Register: priority level 3
    - Interrupt Service Routine Priority Register: priority level 6
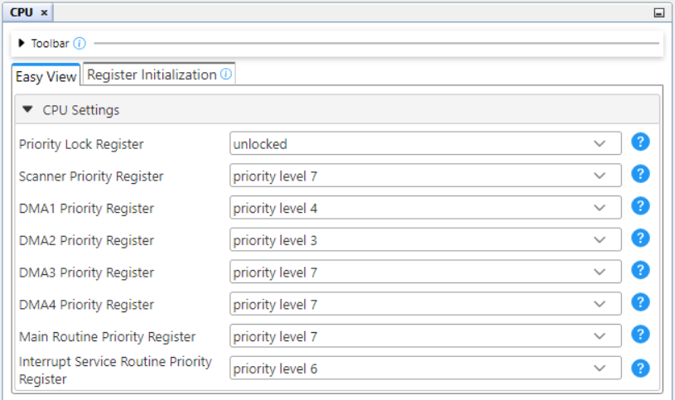
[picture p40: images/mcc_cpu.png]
    <br>
    <br>DMA2 is used to generate the sine wave and need to have the highest priority.

24. Interrupt Manager
    <br>

25. Pins
    <br>

| Pin | Configuration  |          Description         | Custom name |
| :-: | :------------: | :--------------------------: |:-----------:|
| RD6 |  Analog output |        CLC3 output           |      -      |
| RC6 | Digital output |          SPI1 SCK            |      -      |
| RC5 | Digital input  |          SPI1 SDI            |      -      |
| RC2 | Digital output |          SPI1 SDO            |      -      |
| RB0 | Analog output  |          PWM2OUT1            |      -      |
| RF2 | Analog output  |          PWM1OUT1            |      -      |
| RB5 | Digital input  |          UART2 RX            |      -      |
| RB4 | Digital output |          UART2 TX            |      -      |
| RA1 |  Analog input  |  ADC positive input channel  |      -      |
| RA0 | Digital input  |      Button input pin        |   BUTTON    |
| RA4 | Digital output |      OLED board RW pin       |  oledC_RW   |
| RA5 | Digital output |    RLC Meter board CS pin    |   RLC_CS    |
| RA6 | Digital output |          Debug pin           |  DEBUG_PIN  |
| RB2 | Digital output |      OLED board DC pin       |  oledC_DC   |
| RC7 | Digital output |        On-board LED          |  DEBUG_LED  |
| RF4 | Digital output |      OLED board EN pin       |  oledC_EN   | 
| RF5 | Digital output |      OLED board RST pin      |  oledC_RST  | 
| RF7 | Digital output |      OLED board CS pin       |  oledC_nCS  | 
| RW0 | Digital input  |      CLC8IN0 / CLC3IN0       |      -      |
| RW1 | Digital input  |           CLC6IN1            |      -      |
| RW2 | Digital input  |           CLC7IN2            |      -      | 

## Demo

In order to demonstrate the capabilities of this application, a 1 μF capacitor measurement was performed. The result can be seen in the following picture.

<br>

The result can also be visualised in [MPLAB Data Visualizer](https://www.microchip.com/en-us/tools-resources/debug/mplab-data-visualizer?utm_source=GitHub&utm_medium=TextLink&utm_campaign=MCU8_PIC18-Q71&utm_content=pic18f56q71-rlc-meter-mplab-mcc-github&utm_bu=MCU08).
<br>

## Summary

This project showcases the PIC18F56Q71 peripherals' capabilities in a measurement application. For this case, the majority of peripherals are used to create a complex use case.

##  How to Program the Curiosity Nano Board 

This chapter demonstrates how to use the MPLAB X IDE to program a PIC® device with an Example_Project.X. This is applicable to other projects.

1.  Connect the board to the PC.

2.  Open the Example_Project.X project in MPLAB X IDE.

3.  Set the Example_Project.X project as main project.
    <br>Right click the project in the **Projects** tab and click **Set as Main Project**.
    <br>

4.  Clean and build the Example_Project.X project.
    <br>Right click the **Example_Project.X** project and select **Clean and Build**.
    <br>

5.  Select **PICxxxxx Curiosity Nano** in the Connected Hardware Tool section of the project settings:
    <br>Right click the project and click **Properties**.
    <br>Click the arrow under the Connected Hardware Tool.
    <br>Select **PICxxxxx Curiosity Nano** (click the **SN**), click **Apply** and then click **OK**:
    <br>

6.  Program the project to the board.
    <br>Right click the project and click **Make and Program Device**.
    <br>

<br>

- - - 
## Menu
- [Back to Top](#rlc-meter-using-the-pic18f56q71-microcontroller-with-mcc-melody)
- [Back to Related Documentation](#related-documentation)
- [Back to Software Used](#software-used)
- [Back to Hardware Used](#hardware-used)
- [Back to Operation](#operation)
- [Back to Concept](#concept)
- [Back to Setup](#setup)
- [Back to Demo](#demo)
- [Back to Summary](#summary)
- [Back to How to Program the Curiosity Nano Board](#how-to-program-the-curiosity-nano-board)

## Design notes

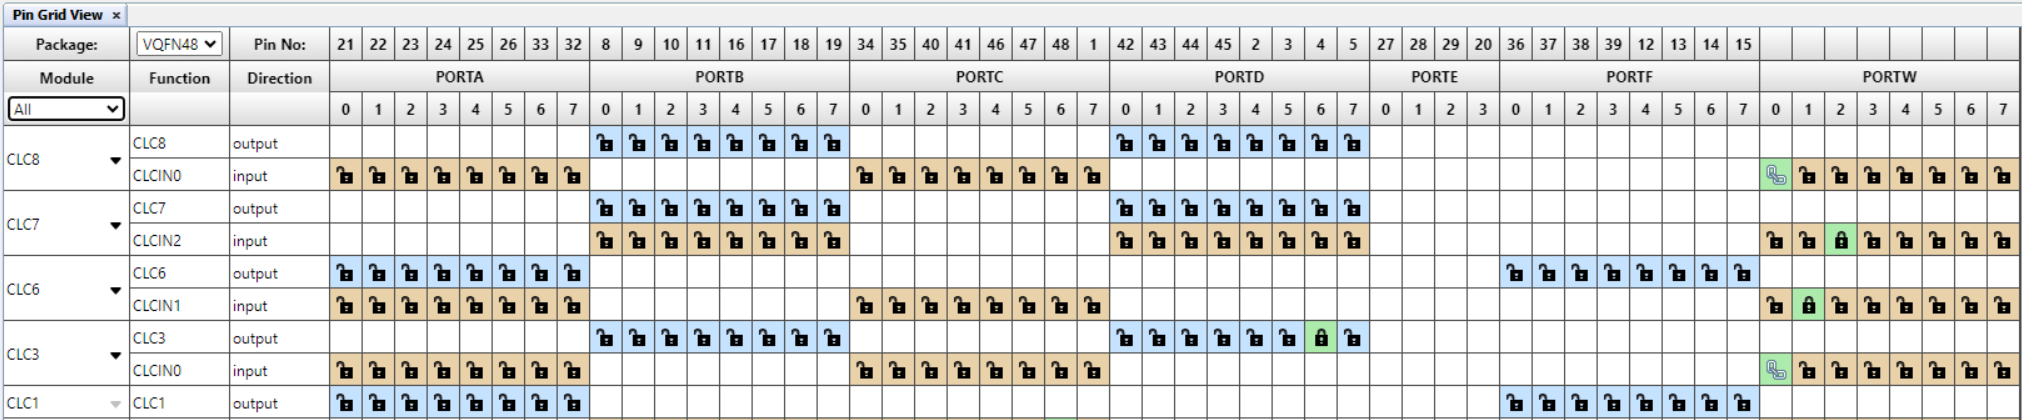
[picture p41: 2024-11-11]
images/mcc_pin_grid_clc.png

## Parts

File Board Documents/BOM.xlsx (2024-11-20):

Bill of Materials | **
Part Number: | EV** | M
Assy Number: | 02-**
PCB Number: | 04-**
Assy Revision: | 1
Creation Date: | 11/5/2024
Designator | Description | Manufacturer | Part Number
C1 | CAP CER 0.015uF 16V 10% X7R SMD 0603 | Panasonic | ECJ-1VB1C153K
C2 | CAP CER 8200pF 50V 10% X7R SMD 0603 | Panasonic | ECJ-1VB1H822K
C3, C4 | CAP CER 1uF 16V 10% X5R SMD 0603 | D5_AVX | 0603YD105KAT2A
C5, C6, C7, C8, C9 | CAP CER 0.1uF 25V 10% X5R SMD 0603 | AVX | 06033D104KAT2A
D1 | DIO LED GREEN 2.05V 10mA CLEAR SMD 0603 | Panasonic Electronic Components Panasonic Electronic Components | LNJ326W83RA
J1 | CON HDR-2.54 FEMALE 1x2 TIN 6MH TH VERT | Sullins Connector Solutions | PPTC021LFBN-RC
R1 | RES TF 6.34k 0.1% 1/10W SMD 0603 AEC-Q200 | Panasonic Electronic Components | ERA-3AEB6341V
R2 | RES TKF 20k 1% 1/10W SMD 0603 CRCW060320K0FKEA AEC-Q200 RS | Vishay Dale | CRCW060320K0FKEA
R3, R4, R13, R14, R15, R16, R18, R19 | RES TKF 1k 5% 1/10W SMD 0603 | Panasonic | ERJ-3GEYJ102V
R5, R6, R7, R8 | RES TKF 100R 5% 1/10W SMD 0603 | Vishay | CRCW0603100RJNEA
R11, R12 | RES TF 10k 1% 1/16W SMD 0603 | TE Connectivity Passive Product | CPF0603F10KC1
R17, R20, R21 | RES SMD 0 OHM JUMPER 0603 | SUSUMU | YJP1608-R001
Microchip Parts
U1, U4 | MCHP ANALOG OPAMP 2-Ch 10MHz MCP6022-E/ST TSSOP-8 | Microchip Technology | MCP6022-E/ST
U2, U3 | MCHP ANALOG PGA 8-Ch 12MHz MCP6S26T-I/SL SOIC-14 | Microchip | MCP6S26T-I/SL
U5 | MCHP ANALOG LDO 3.3V MCP1700T-3302E/TT SOT-23-3 | Microchip Technology | MCP1700T-3302E/TT
Mechanical Parts
LABEL? | LABEL PCBA 18x6mm Datamatrix Assy# / Rev / Serial / Date | ACT Logimark AS | 505462

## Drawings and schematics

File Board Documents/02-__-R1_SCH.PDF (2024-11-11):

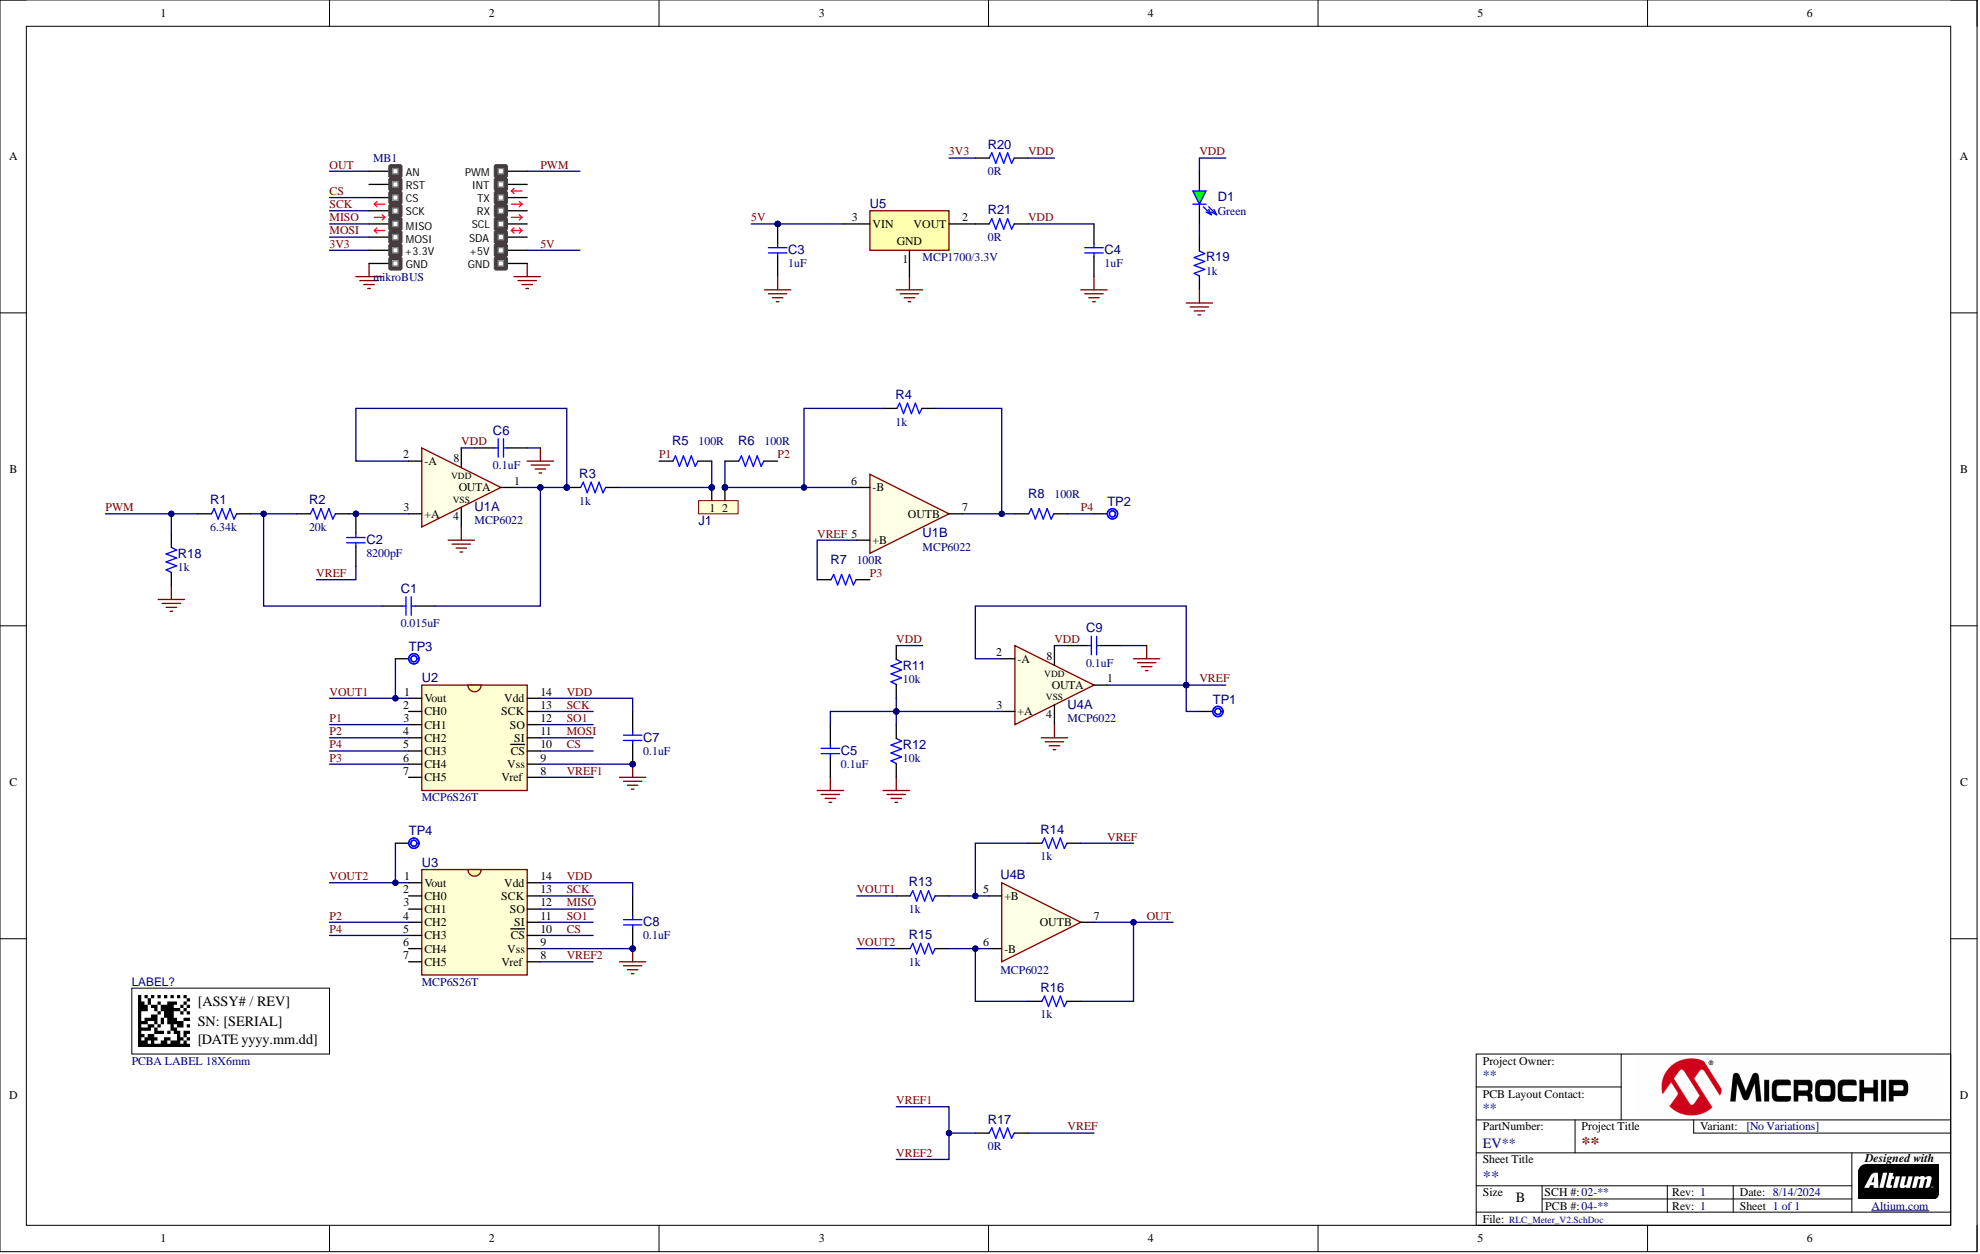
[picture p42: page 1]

[ASSY# / REV]
SN: [SERIAL]
[DATE yyyy.mm.dd]

Sheet Title ** | Designed with Altium.com

Size B | SCH #: 02-** | Rev: 1 | Date: 8/14/2024

PCB #: 04-** | Rev: 1 | Sheet

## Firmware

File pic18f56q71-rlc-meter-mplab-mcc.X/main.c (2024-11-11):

 /*
 * MAIN Generated Driver File
 * 
 * @file main.c
 * 
 * @defgroup main MAIN
 * 
 * @brief This is the generated driver implementation file for the MAIN driver.
 *
 * @version MAIN Driver Version 1.0.2
 *
 * @version Package Version: 3.1.2
*/

/*
� [2024] Microchip Technology Inc. and its subsidiaries.

    Subject to your compliance with these terms, you may use Microchip 
    software and any derivatives exclusively with Microchip products. 
    You are responsible for complying with 3rd party license terms  
    applicable to your use of 3rd party software (including open source  
    software) that may accompany Microchip software. SOFTWARE IS ?AS IS.? 
    NO WARRANTIES, WHETHER EXPRESS, IMPLIED OR STATUTORY, APPLY TO THIS 
    SOFTWARE, INCLUDING ANY IMPLIED WARRANTIES OF NON-INFRINGEMENT,  
    MERCHANTABILITY, OR FITNESS FOR A PARTICULAR PURPOSE. IN NO EVENT 
    WILL MICROCHIP BE LIABLE FOR ANY INDIRECT, SPECIAL, PUNITIVE, 
    INCIDENTAL OR CONSEQUENTIAL LOSS, DAMAGE, COST OR EXPENSE OF ANY 
    KIND WHATSOEVER RELATED TO THE SOFTWARE, HOWEVER CAUSED, EVEN IF 
    MICROCHIP HAS BEEN ADVISED OF THE POSSIBILITY OR THE DAMAGES ARE 
    FORESEEABLE. TO THE FULLEST EXTENT ALLOWED BY LAW, MICROCHIP?S 
    TOTAL LIABILITY ON ALL CLAIMS RELATED TO THE SOFTWARE WILL NOT 
    EXCEED AMOUNT OF FEES, IF ANY, YOU PAID DIRECTLY TO MICROCHIP FOR 
    THIS SOFTWARE.
*/
#include "mcc_generated_files/system/system.h"
#include "mcp6s26.h"
#include "rlc.h"
#include "display.h"

/*
    Main application
*/

/* 
    SAMPLE_NO - number of complete waveform used for computation
    SAMPLE_NO_AUTOGAIN - number of complete waveform used for computation for auto gain algorithm
    CALIBRATION_REPEAT_NO - repeat number for calibration process
*/
#define SAMPLE_NO                   16
#define SAMPLE_NO_AUTOGAIN          4
#define CALIBRATION_REPEAT_NO       8

#define CALIBRATION_DATA_ADDRESS    (EEPROM_START_ADDRESS)
#define CALIBRATION_DONE_STATUS     (0xAA)

extern uint8_t adcSamplesArray1[512];
extern uint8_t adcSamplesArray3[512];

int16_t voltageSampleArray[WAVE_STEPS];
int16_t currentSampleArray[WAVE_STEPS];

uint32_t voltageRealMax;
uint32_t voltageImagMax;
uint32_t currentRealMax;
uint32_t currentImagMax;

float oldZReal = 0.0, oldZImag = 0.0;
float oldVRealUnscaled = 0.0, oldVImagUnscaled = 0.0, oldIRealUnscaled = 0.0, oldIImagUnscaled = 0.0;

volatile bool dma1TransferEnded = false;
volatile bool dma3TransferEnded = false;
volatile bool dmaTransferDone = false;
volatile bool buttonShortPress = false;
volatile bool buttonLongPress = false;
volatile bool buttonPress = false;
volatile uint8_t vGainIndex = MCP6S26_GAIN_1X;
volatile uint8_t iGainIndex = MCP6S26_GAIN_1X;

static calibration_state_t calibrationState = VOLTAGE_PREPARE;
static int16_t *adcValue;
static uint8_t dmaCounter;

enum COMPONENT component = CAPACITOR;

void Button_Handler(void)
{
    __delay_ms(10); // Debouncing
    if(!(BUTTON_GetValue() & 0x01))
    {
       buttonPress = true;
       TMR2_Write(0x00);
       TMR2_Start(); 
    }
    else if(buttonPress)
    {
        buttonPress = false;
        buttonShortPress = true;
        TMR2_Stop();
    }
}

void TMR2_Handler(void)
{
    buttonLongPress = true;
    buttonPress = false;
    TMR2_Stop();
}

void PWM2_Set_Autoload_Trigger(void)
{
    //PWMLDS DMA2_Destination_Count_Done;
    PWM2LDS = 0xC;
}

void DMA1_Transfer_Ended_Handler(void)
{
    dmaCounter--; 
    if (dmaCounter == 0)
    {
        DisableADCTrigger();
        dmaTransferDone = true;
    }
    else
    {
        DMA3_TransferWithTriggerStart();
    }
    dma1TransferEnded = true;        
    DEBUG_PIN1_Toggle();
}

void DMA3_Transfer_Ended_Handler(void)
{
    dmaCounter--; 
    if (dmaCounter == 0)
    {
        DisableADCTrigger();
        dmaTransferDone = true;
    } 
    else
    {
        DMA1_TransferWithTriggerStart();
    }
    dma3TransferEnded = true;        
    DEBUG_PIN1_Toggle();
}

void Get_Raw_Data(uint8_t noSamples, int16_t* dataBuffer)
{
    static bool rawDataReady;
    
    rawDataReady = false;
    
    dmaCounter = noSamples;
    dma1TransferEnded = false;    
    dma3TransferEnded = false;
    dmaTransferDone = false;
    
    for (uint8_t i = 0; i < WAVE_STEPS; i++)
    {
        dataBuffer[i] = 0;
    }
    
    DEBUG_LED_Toggle();
    
    DMA1_TransferWithTriggerStart();
    EnableADCTrigger();
    
    while (rawDataReady == false)
    {
       if (dma1TransferEnded == true)
       {
            adcValue = (int16_t*)adcSamplesArray1;
            for (uint8_t i = 0; i < WAVE_STEPS; i++)
            {
                dataBuffer[i] += adcValue[i];
            }           
            dma1TransferEnded = false;  
       }
       
       if (dma3TransferEnded == true)
       {
            adcValue = (int16_t*)adcSamplesArray3;
            for (uint8_t i = 0; i < WAVE_STEPS; i++)
            {
                dataBuffer[i] += adcValue[i];
            }
            dma3TransferEnded = false;  
       }    
       
       if ((dmaTransferDone == true) && (dma1TransferEnded == false) && (dma3TransferEnded == false))
       {
           rawDataReady = true;
       }
    }
    
    DEBUG_LED_Toggle();
}

float Abs_Val(float x)
{
    return x > 0.0 ? x : (-1.0 * x);
}

void EEPROM_Write_Double_Word(eeprom_address_t address, uint32_t data)
{
    eeprom_data_t tmpData;
    
    NVM_UnlockKeySet(UNLOCK_KEY);
    
    tmpData = (uint8_t)((data & 0xFF000000) >> 24);
    while(NVM_IsBusy());
    EEPROM_Write(address, tmpData);
    
    tmpData = (uint8_t)((data & 0x00FF0000) >> 16);
    while(NVM_IsBusy());
    EEPROM_Write(address + 1, tmpData);
    
    tmpData = (uint8_t)((data & 0x0000FF00) >> 8);
    while(NVM_IsBusy());
    EEPROM_Write(address + 2, tmpData);
    
    tmpData = (uint8_t)((data & 0x000000FF) >> 0);
    while(NVM_IsBusy());
    EEPROM_Write(address + 3, tmpData);
    
    NVM_UnlockKeyClear();
}

bool Check_Calibration_Mode(bool calibrationMode)
{
    if(buttonLongPress == true)
    {
        buttonLongPress = false;
            
        if(calibrationMode == false)
        {
            calibrationMode = true;
            calibrationState = VOLTAGE_PREPARE;
                
            printf("\n\rEnter calibration mode. Long press the button for exit.\n\r");
            Display_Message("Calibration mode", "Long press exit");
            __delay_ms(1000);
        }
            
        else
        {
            calibrationMode = false;
            printf("\n\rExit calibration mode.\n\r");
            Display_Message("", "");
        }
    }
    
    return calibrationMode;
}

bool Calibration_Process(void)
{
    static uint32_t voltageRealCalibrationValue = 0;
    static uint32_t voltageImagCalibrationValue = 0;
    static uint32_t currentRealCalibrationValue = 0;
    static uint32_t currentImagCalibrationValue = 0;
    
    switch(calibrationState)
    {
        case VOLTAGE_PREPARE:
        {
            printf("\n\r");
            printf("Voltage calibration\n\r");
            printf("DUT must not be inserted\n\r");
            printf("Short press to start the calibration\n\r\n\r");
            Display_Message("Voltage calib", "DUT not connect");
                    
            calibrationState = VOLTAGE_CALIBRATION;
                    
            break;
        }
                
        case VOLTAGE_CALIBRATION:
        {
            if(buttonShortPress == true)
            {
                buttonShortPress = false;
                        
                printf("Calibration...\n\r");
                Display_Message("Calibration...", "");
                        
                voltageRealCalibrationValue = 0;
                voltageImagCalibrationValue = 0;
                
                uint8_t vGainIndex = MCP6S26_GAIN_1X;
                        
                SelectVoltage();

                GainSet(vGainIndex);
                Set_VGain(vGainIndex);

                __delay_ms(7); 
                
                for(uint8_t i = 0; i < CALIBRATION_REPEAT_NO; i++)
                {
                    Get_Raw_Data(1, voltageSampleArray);

                    Process_Impedance_Values();
                    
                    // The maximum value is considered to be 40% grater than the read value
                    voltageRealCalibrationValue += (uint32_t)(1.4 * Abs_Val(Get_VRealUnscaled()));
                    voltageImagCalibrationValue += (uint32_t)(1.4 * Abs_Val(Get_VImagUnscaled()));
                }
                
                calibrationState = CURRENT_PREPARE;
            }
                    
            break;
        }
                
        case CURRENT_PREPARE:
        {
            printf("\n\r");
            printf("Current calibration\n\r");
            printf("The DUT terminals must be in short circuit\n\r");
            printf("Short press to start the calibration\n\r\n\r");
            Display_Message("Current calib", "DUT in short");
                    
            calibrationState = CURRENT_CALIBRATION;
                    
            break;
        }
                
        case CURRENT_CALIBRATION:
        {
            if(buttonShortPress == true)
            {
                buttonShortPress = false;
                        
                printf("Calibration...\n\r");
                Display_Message("Calibration...", "");
                        
                currentRealCalibrationValue = 0;
                currentImagCalibrationValue = 0;
                
                uint8_t iGainIndex = MCP6S26_GAIN_1X;

                SelectCurrent();

                GainSet(iGainIndex);
                Set_IGain(iGainIndex);

                __delay_ms(13);
                
                for(uint8_t i = 0; i < CALIBRATION_REPEAT_NO; i++)
                { 
                    Get_Raw_Data(1, currentSampleArray);
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

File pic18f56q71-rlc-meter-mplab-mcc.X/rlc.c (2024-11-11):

 /*
 * RLC File
 * 
 * @file rlc.c
 * 
 * @defgroup rlc
 * 
 * @brief This file contains the implementation of the RLC functions.
*/

/*
© [2024] Microchip Technology Inc. and its subsidiaries.

    Subject to your compliance with these terms, you may use Microchip 
    software and any derivatives exclusively with Microchip products. 
    You are responsible for complying with 3rd party license terms  
    applicable to your use of 3rd party software (including open source  
    software) that may accompany Microchip software. SOFTWARE IS ?AS IS.? 
    NO WARRANTIES, WHETHER EXPRESS, IMPLIED OR STATUTORY, APPLY TO THIS 
    SOFTWARE, INCLUDING ANY IMPLIED WARRANTIES OF NON-INFRINGEMENT,  
    MERCHANTABILITY, OR FITNESS FOR A PARTICULAR PURPOSE. IN NO EVENT 
    WILL MICROCHIP BE LIABLE FOR ANY INDIRECT, SPECIAL, PUNITIVE, 
    INCIDENTAL OR CONSEQUENTIAL LOSS, DAMAGE, COST OR EXPENSE OF ANY 
    KIND WHATSOEVER RELATED TO THE SOFTWARE, HOWEVER CAUSED, EVEN IF 
    MICROCHIP HAS BEEN ADVISED OF THE POSSIBILITY OR THE DAMAGES ARE 
    FORESEEABLE. TO THE FULLEST EXTENT ALLOWED BY LAW, MICROCHIP?S 
    TOTAL LIABILITY ON ALL CLAIMS RELATED TO THE SOFTWARE WILL NOT 
    EXCEED AMOUNT OF FEES, IF ANY, YOU PAID DIRECTLY TO MICROCHIP FOR 
    THIS SOFTWARE.
*/
#include <xc.h>
#include "rlc.h"
#include "math.h"

extern int16_t voltageSampleArray[WAVE_STEPS];
extern int16_t currentSampleArray[WAVE_STEPS];

float vReal_Raw, vImag_Raw, iReal_Raw, iImag_Raw;
float vRealUnscaled, vImagUnscaled, iRealUnscaled, iImagUnscaled;

static float zReal_Raw, zImag_Raw, yReal_Raw, yImag_Raw;
static float zMod, zArg;
static float vGain, iGain;

float Get_Sin(uint8_t index)
{
    if (index >=   0 &&  index < 63 ) return sinTable[index];
    if (index >=  63 &&  index < 125 )  return (sinTable[125 - index]);
    if (index >= 125 &&  index < 188 ) return (-1.0 * sinTable[index - 125]);
    if (index >= 188 &&  index < 250 )  return (-1.0 * sinTable[250 - index]);
}

float Get_Cos(uint8_t index)
{
    if (index >= 0   &&  index < 63 ) return cosTable[index];
    if (index >= 63  &&  index < 125 )  return (-1.0 * cosTable[125 - index]);
    if (index >= 125 &&  index < 188 ) return (-1.0 * cosTable[index - 125]);
    if (index >= 188 &&  index < 250 )  return (cosTable[250 - index]);
}

void Process_Impedance_Values(void)
{ 
    uint16_t index = 0;
    
    vReal_Raw = 0.0;
    vImag_Raw = 0.0;
    iReal_Raw = 0.0;
    iImag_Raw = 0.0;

    for (uint16_t i = 0; i < WAVE_STEPS; i++)
    {
        index  = (i * timesamplingRates[TIMESAMPLING_RATE]) % WAVE_STEPS;
        vReal_Raw = vReal_Raw + (float)(voltageSampleArray[i] * 1.0) * (float)Get_Cos(index);
        vImag_Raw = vImag_Raw + (float)(voltageSampleArray[i] * 1.0) * (float)Get_Sin(index);
        iReal_Raw = iReal_Raw + (float)(currentSampleArray[i] * 1.0) * (float)Get_Cos(index);
        iImag_Raw = iImag_Raw + (float)(currentSampleArray[i] * 1.0) * (float)Get_Sin(index);
    }
    
    vRealUnscaled = vReal_Raw;
    vImagUnscaled = vImag_Raw;
    iRealUnscaled = iReal_Raw;
    iImagUnscaled = iImag_Raw;
   
    /* Scale by gain */     
    vReal_Raw = 1000.0 * vReal_Raw / vGain ;
    vImag_Raw = 1000.0 * vImag_Raw / vGain ;
    iReal_Raw = -1.0 * iReal_Raw / iGain ;
    iImag_Raw = -1.0 * iImag_Raw / iGain ;
     
    /* Impedance calculation, no compensation */
    zReal_Raw = (float)(vReal_Raw * iReal_Raw + vImag_Raw * iImag_Raw)/(float)(iReal_Raw * iReal_Raw + iImag_Raw * iImag_Raw);   
    zImag_Raw = (float)(vImag_Raw * iReal_Raw - vReal_Raw * iImag_Raw)/(float)(iReal_Raw * iReal_Raw + iImag_Raw * iImag_Raw);   
    
    zMod = sqrt(zReal_Raw * zReal_Raw + zImag_Raw * zImag_Raw);
    zArg = atan2(zImag_Raw, zReal_Raw);
}

float Get_ZReal(void)
{
    return zReal_Raw;
}

float Get_ZImag(void)
{
    return zImag_Raw;
}

float Get_VReal(void)
{
    return vReal_Raw;
}

float Get_VImag(void)
{
    return vImag_Raw;
}

float Get_IReal(void)
{
    return iReal_Raw;
}

float Get_IImag(void)
{
    return iImag_Raw;
}

float Get_ZArg(void)
{
    return zArg;
}

float Get_ZMod(void)
{
    return zMod;
}

float Get_VRealUnscaled(void)
{
    return vRealUnscaled;
}

float Get_VImagUnscaled(void)
{
    return vImagUnscaled;
}

float Get_IRealUnscaled(void)
{
    return iRealUnscaled;
}

float Get_IImagUnscaled(void)
{
    return iImagUnscaled;
}

float Get_Gain(uint8_t index)
{
    return opaGainTable[index];
}

void Set_VGain(uint8_t index)
{
    if (index > 7) vGain = 1.00;
    else vGain = opaGainTable[index];
}

void Set_IGain(uint8_t index)
{
    if (index > 7) iGain = 1.00;
    else iGain = opaGainTable[index];
}

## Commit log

2024-11-11 MPAE-18878: Update code, readme and metadata
    [04-__-R1.GBL, 04-__-R1.GBO, 04-__-R1.GBS, 04-__-R1.GTL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]
2024-11-20 MPAE-18878: Implement review
    [BOM.xlsx]
